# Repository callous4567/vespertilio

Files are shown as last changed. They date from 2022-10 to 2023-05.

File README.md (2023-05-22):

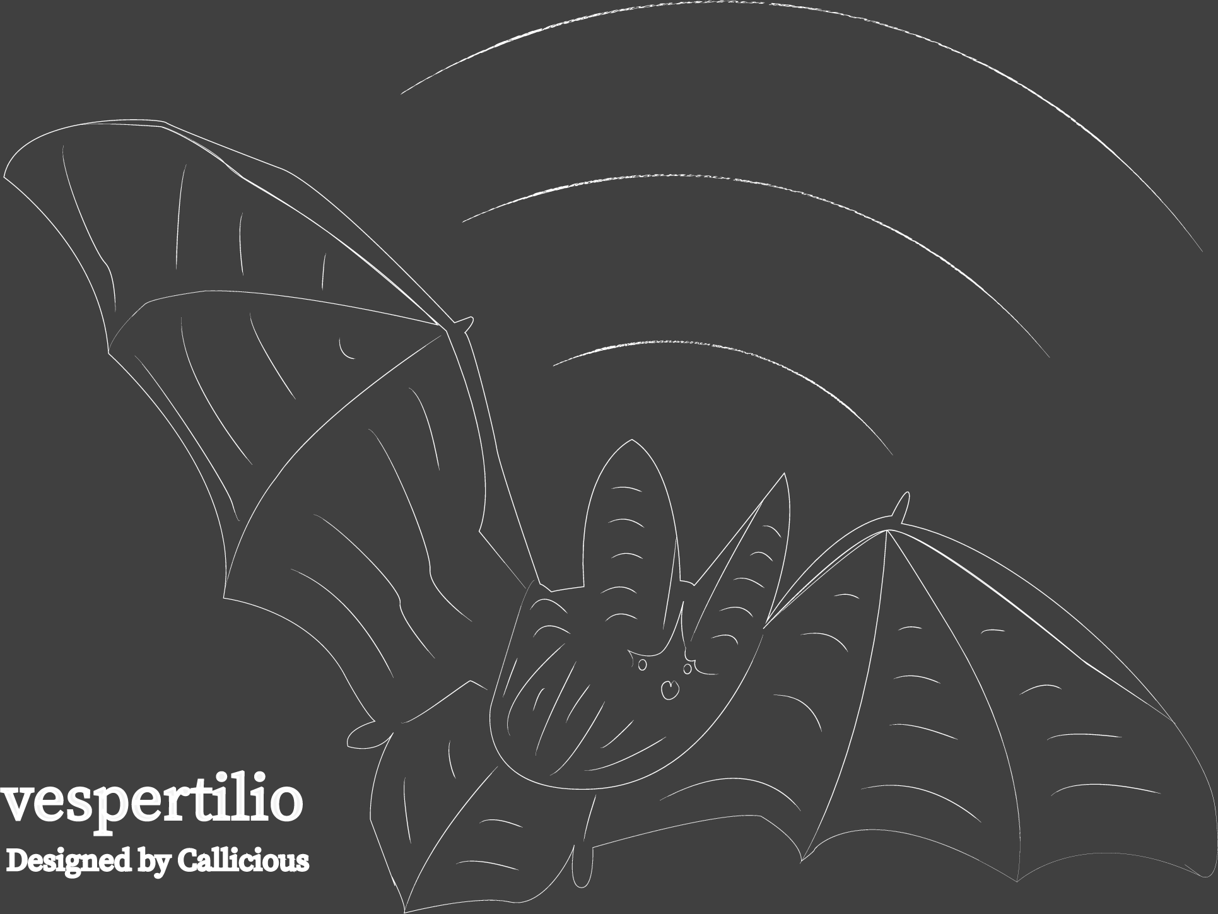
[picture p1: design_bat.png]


## General description 
A battery-powered bioacoustic recorder with a built-in ambient light sensor, and an optional weather-sensing addon attached by an onboard hijacked USB-C connector! Very much a WIP!

This is my first time with C (embedded or otherwise) and with a bunch of other things- PCBs, electronics, 3D CAD/printing/etc, so you will have to bare with me whilst I work through this project bit by bit 😅

## Where is it at the moment?
V6 design complete and functional code-wise/hardware-wise, with 75 mA power use @ 384 ksps with 12-bit internal RP2040 ADC. V9 design in progress, aiming for 50 mA power use @ 384 ksps with 16-bit dedicated ADC- hardware stage (firmware t.b.d.) 

## Features 
- BME280 for Environmental Sensing (Temp, Pressure, Humidity) as an optional attachment (attached to environmental case with 6-core custom USB-C cable!) 
- Knowles Winfrey Microphone with Differential Amplifier -> Inverting Amplifier Cascade for audio (giving single-ended-equivalent gains minimum 220+!)
- Vishay VEML6040A3OG to provide ambient light sensing of the environment
- 4-way PGA secondary gain on cascaded differential-inverting amplifier
- Compatible with usual MicroSD cards FAT32/exFAT/... @ up to 480 ksps sample rate 
- Supercapacitor on RTC allows upwards of 15 minutes to exchange batteries without losing timing configuration- no need to reconfigure after re-batterying... battery-re.. whatever!
- Competitive BOM cost: roughly £55 as of Ver 9 inclusive of weather sensor, which adds about £10 to the final cost.
- USB configurable recording schedules using desktop .exe and .json. **WIP**, allow for setting sampling frequency with each session, too, and make a GUI for configuration. **WIP**, also set the firmware over USB without having to toggle bootsel on the Pico. 

## Todo/current
- (!!!Extremely immediate!!!) Coding/Designing V9 PCB arrangement, which has 16-bit MCP33131 500ksps ADC instead, and analogue PGA switch arrangement for gain control. 
- (!!!Extremely immediate!!!) V9 PCB external regulator board design with dual MAX38640 buck regulators & 2nd-order filter design for digital power supply 
- (Delayed) Weatherproof case designs (for V6+ Audiomoth Scale, V5 done and worked fine.) 

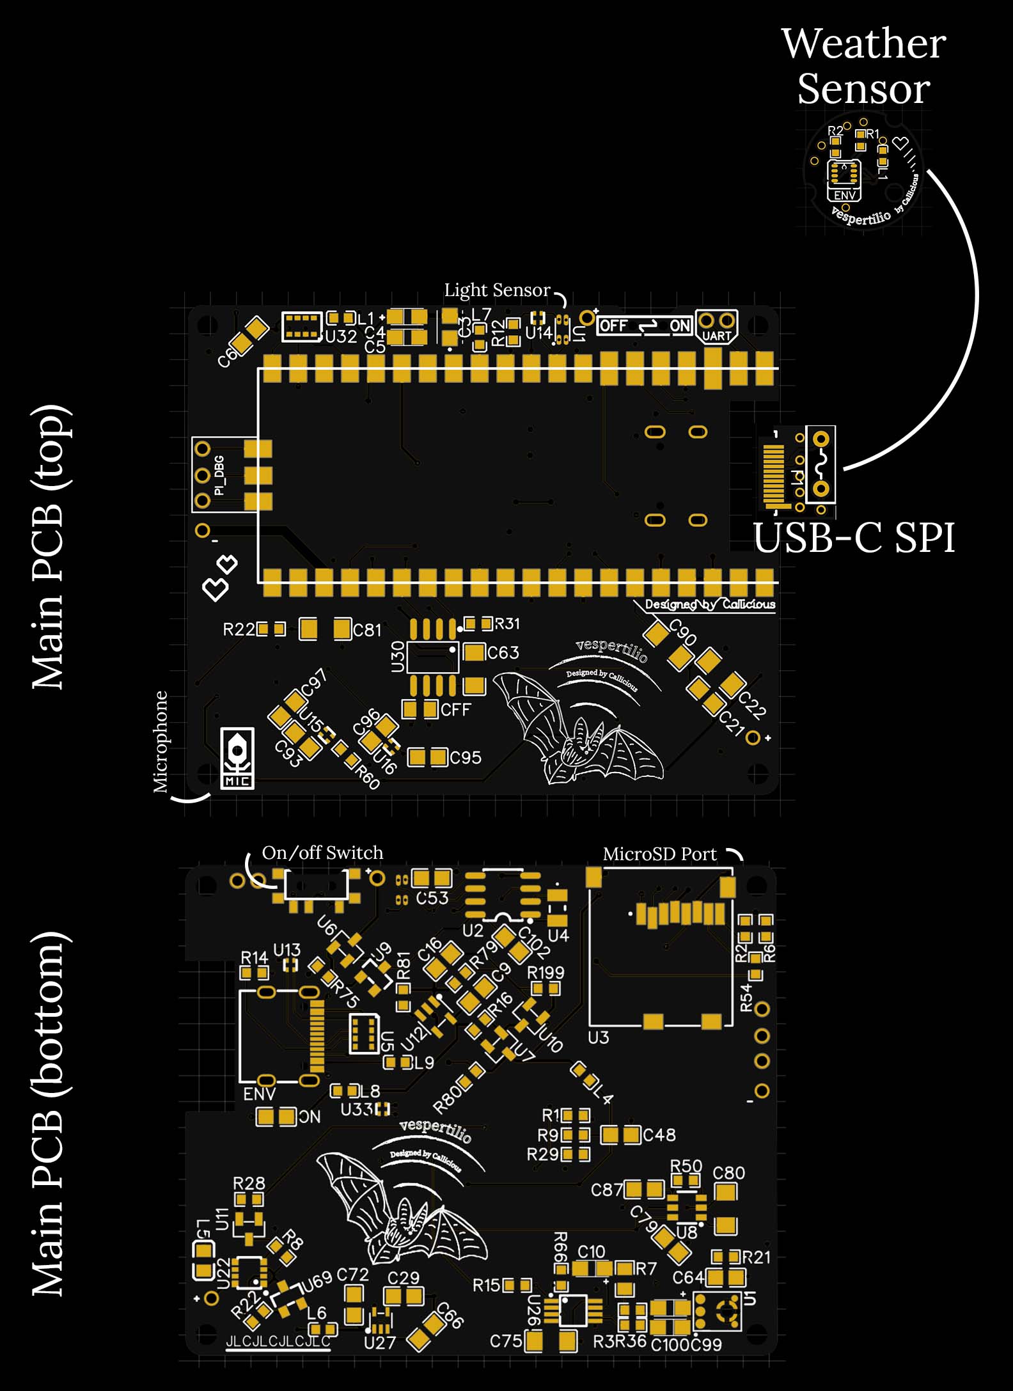
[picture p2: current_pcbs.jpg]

^*The current (outdated*) spread of PCBS and concept. vespertilio is optionally attached, by a USB-C connector manhandled into an SPI connector, to a weather module PCB.
You don't need to use the weather module- doing so costs about £10-ish. The 3D-printed case plans will allow for optional use of it. You'll note that I added that little lightmeter- U1 :)*

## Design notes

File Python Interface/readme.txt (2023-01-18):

This readme.txt will explain how to configure the vespertilio with the included JSON and executable file.
Please refer to https://github.com/callous4567/vespertilio for any updates, information on firmware updates, and so forth.

To start, set the power switch on vespertilio to OFF. 

You must first configure the vespertilio_config JSON file. 
The file will look something like this...

{
    "ADC_SAMPLE_RATE":192000,
    "RECORDING_MINUTES_PER_SUBRECORDING":5,
    "RECORDING_SESSION_LENGTH_MINUTES":120,
    "START_MINUTE":20,
    "START_HOUR":15,
    "USE_BME":true,
    "BME_PERIOD_SECONDS":3
}

ADC_SAMPLE_RATE: in Hz, sampling rate of the device. There is a limit of 499,999 (qualified on a Sandisk Ultra 64 GB to work at 480 kHz)
RECORDING_SESSION_LENGTH_MINUTES: the length of the recording session, in minutes. 
RECORDING_MINUTES_PER_SUBRECORDING: minutes per recording. We must split recording sessions to minimize number of corrupted files.
START_MINUTE: 0:59, which minute to start the recording on. By default, we start at second=0.
START_HOUR: 0:23, which hour to start the recording on.
USE_BME: true-false on whether to use environmental sensing. Note that this may add file delay. 
BME_PERIOD_SECONDS: period, in seconds, for environmental sensing. Higher = better for file delay.

Following configuration of the JSON file, you should save it and then set the power switch on vespertilio to ON.

You should then run the executable included within a minute of doing this. This executable will...

	- Parse JSON file 
	- Retrieve system time 
	- Handshake with vespertilio, send configuration to it, and tell Pico to save it to onboard flash
	- Transfer the system time to the Pico for it to configure the PCB RTC
	- Initiate a wait sequence.

Once complete, and if successful, the vespertilio will spasm its onboard LED in the colour GREEN, signifying success.

At this point, you should disconnect the USB cable and turn off the vespertilio- the order of this step doesn't matter. All success!

If you encounter any red LED flashes during this process, an error has occurred- double check your JSON with an online parser.
If the online parser says it's fine, and if you have ensured that the variables all match the same type as the template above...
Well, in that case you just have to ask me and I will check it- your device might be dogged (unlikely) or the code is busted (likely.)
Oh, or your USB cable is piss.

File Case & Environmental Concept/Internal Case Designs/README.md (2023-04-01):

# Here's the main case design that is currently running (as of PCB Ver. 4+) for the "internal case" that holds the PCB and batteries.
I've included some renders of the front and back. To mount the PCB to it, you just need some self-tapping M2 screws. To set up the battery compartment,
you'll need a soldering iron and the appropriate leaf spring battery clips from Keystone- check the BOM. Oh, and some wire that can handle at least 100 mA.
Some epoxy will help keep the battery clips in place- though it should not be necessary given I've included some indentations to avoid the clips coming loose 
(since they come with a fang to grab hold of 'em.) 

This is a WIP and all of this will be mentioned in the future guide I will write on how to build it/use it.

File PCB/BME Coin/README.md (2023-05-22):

## General description 
Ver. 1 is compatible with all model(s) before Rev. 9 of the mainboard (which is switching to I2C communication rather than SPI.) Ver.2 (t.b.d) should be used with mainboard PCB versions Rev. 9 and above.

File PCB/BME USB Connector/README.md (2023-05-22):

## General description 
Switching to I2C as of Ver. 9 of the mainboard, which will alter the pinout of the USB connector (but the same connector PCB can still be used.)

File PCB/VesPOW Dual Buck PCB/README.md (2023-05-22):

## General description 
Buck PCB to provide 3V3 and 1V1 from input VCC/batteries, with pi filters on all inputs/outputs to minimize noise. Untested and WIP for Ver. 9.

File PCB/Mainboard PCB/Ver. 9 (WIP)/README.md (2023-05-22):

## General description 
This is a placeholder to note that this is a WORK IN PROGRESS PCB! Only V6 has been qualified as fully-functional and satisfactory.

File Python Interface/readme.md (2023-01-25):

# This for the USB configuration of the device
At the moment, this is WIP. The .exe included does work- just follow readme.txt and you will be fine. 

## Planned configuration features
- Vary ADC sampling rate over sessions.
- Bootsel over USB instead of requiring use of the bootsel button on the pico. Should be easy to induce- Picoprobe does it over UART.
- GUI for the configurator- I want to make a real posh one!

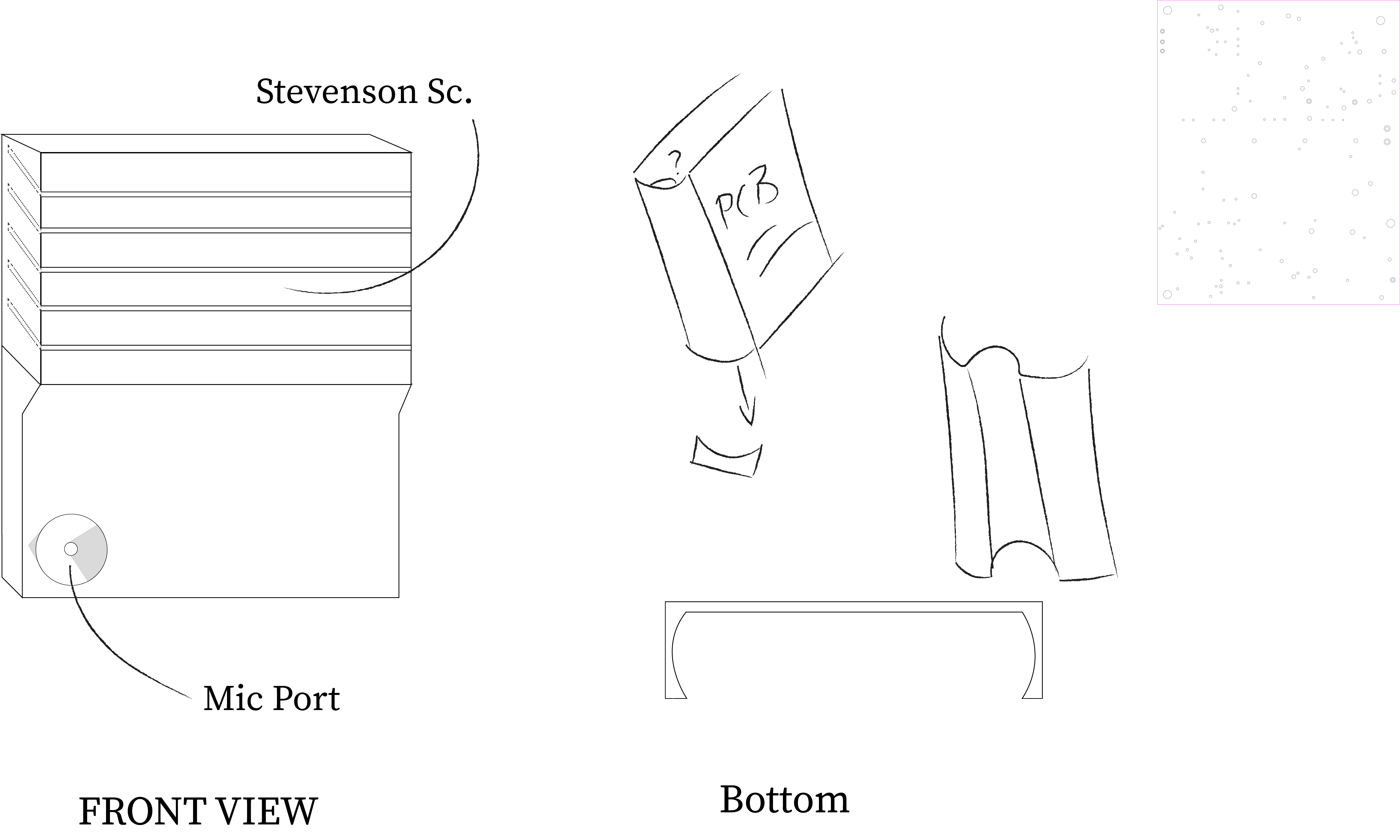
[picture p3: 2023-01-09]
PCB/Silkscreen Design Files/Ver. 3/Design for Pcb enclosure.png

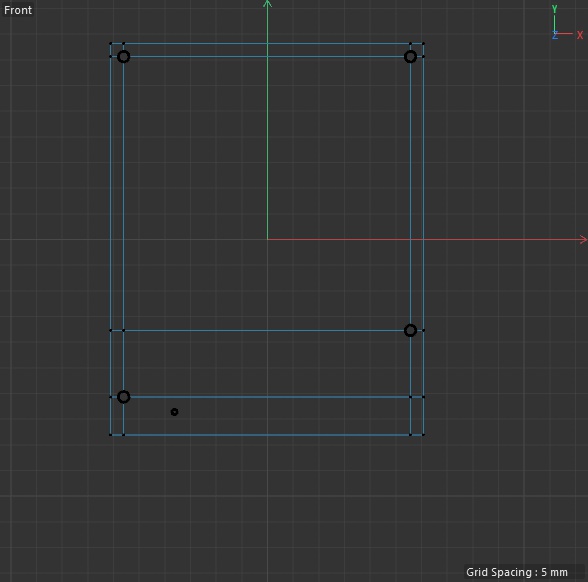
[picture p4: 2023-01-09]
PCB/Silkscreen Design Files/Ver. 3/Image.jpg

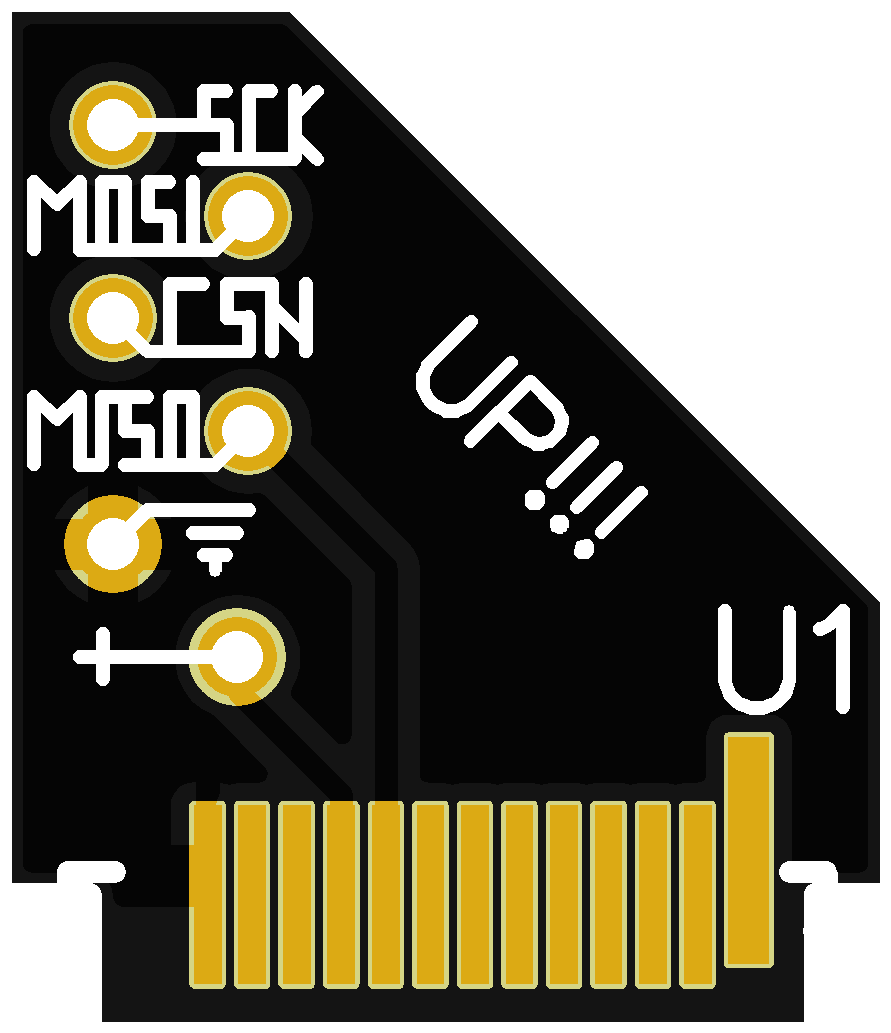
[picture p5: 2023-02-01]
PCB/BME USB Connector/Ver. 4/ex.png

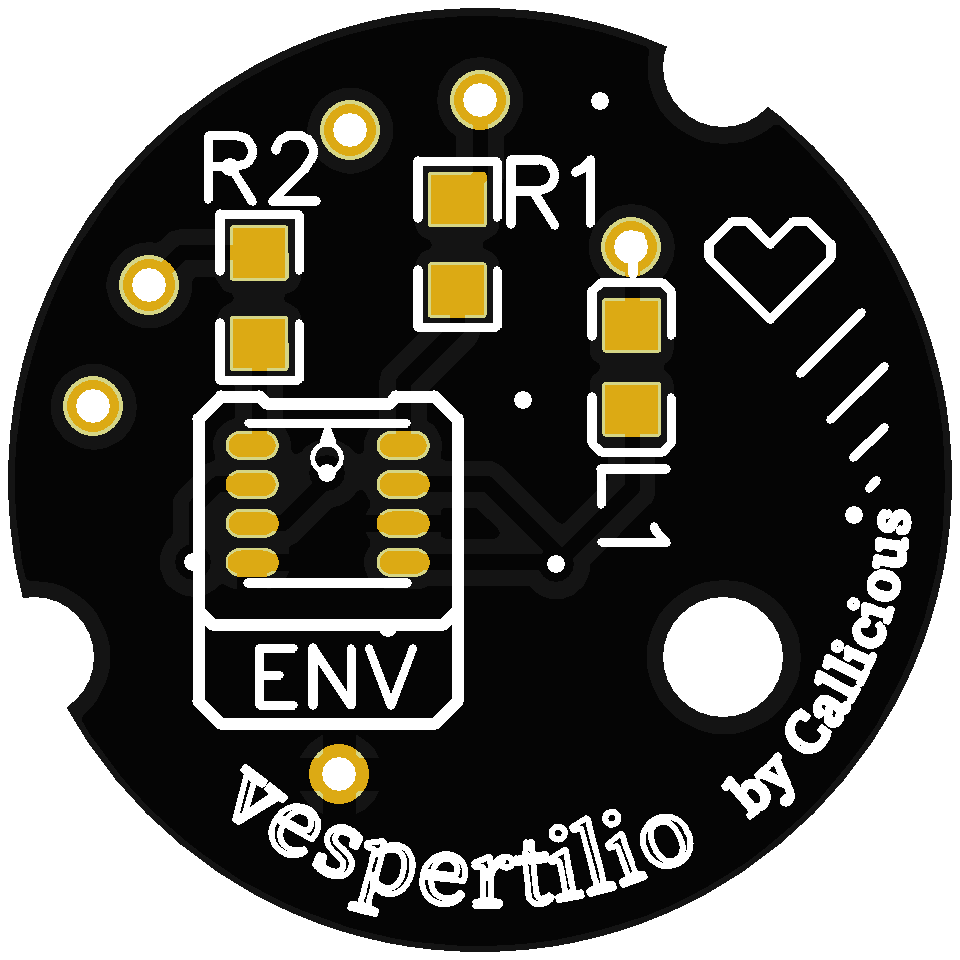
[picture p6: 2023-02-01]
PCB/BME Coin/Ver. 1/ex.png

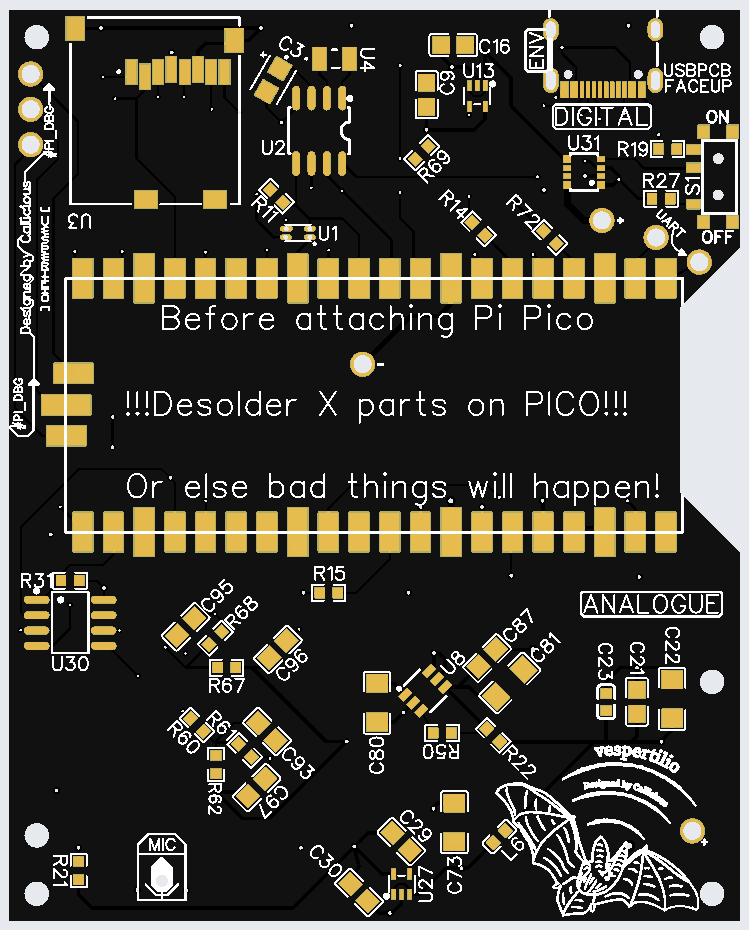
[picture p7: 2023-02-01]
PCB/Mainboard PCB/Ver. 4/ex.PNG

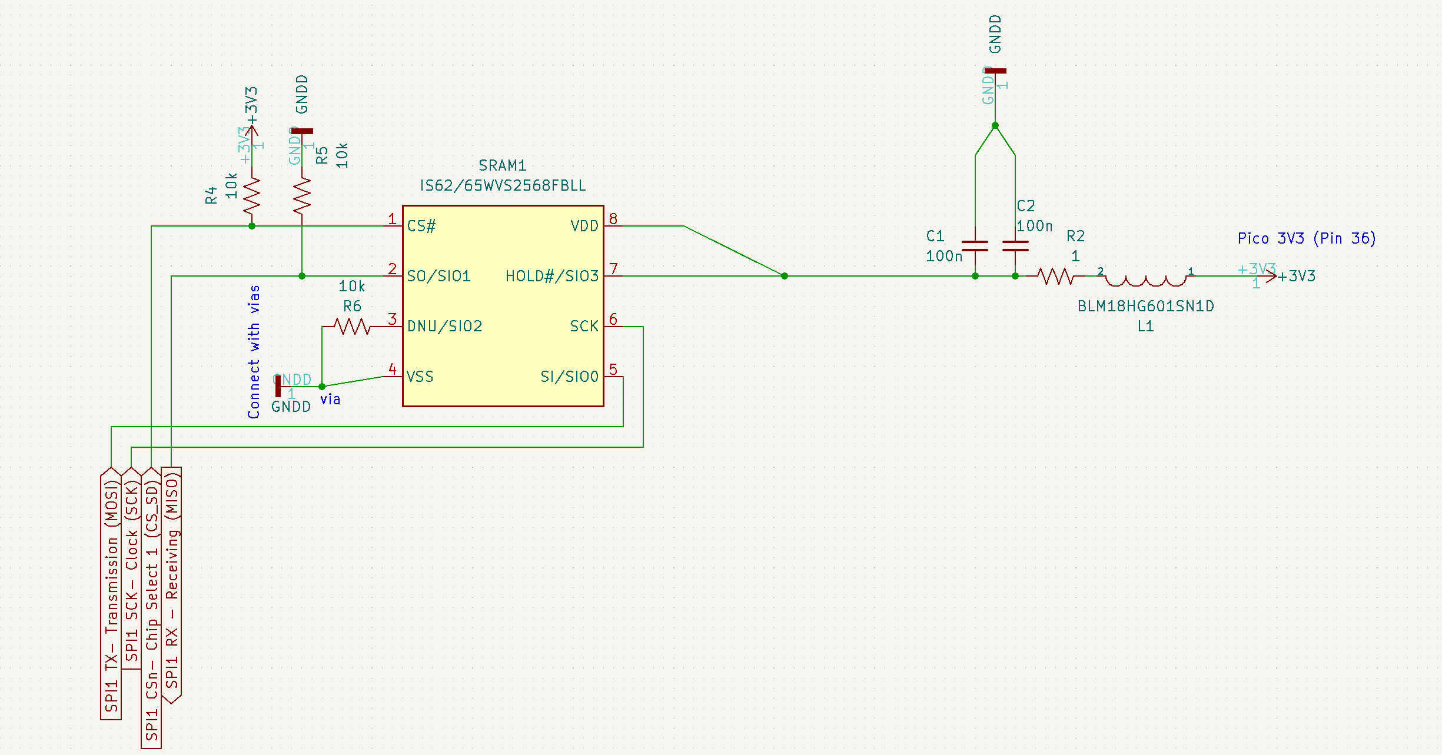
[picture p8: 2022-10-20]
IS62 SPI SRAM Driver/Circuit.PNG

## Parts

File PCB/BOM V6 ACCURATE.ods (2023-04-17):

Component | Value | Type | LCSC Part | Vendor Part | Vendor | Note | Note | Total Count | Cost Per | Total Cost
C3 | 11m | Supercap |  | CPH3225A | Digi-key | SEIKO INSTRUMENTS (VA) |  | 1 | 1.61 | 1.61
C4 | 0.1u | Tantalum | C7173 | TAJA104K035RNJ | LCSC | LOW ESR |  | 2 | 0.398 | 0.796
C5 | 10u | Tantalum | C74423 | TPSA106K010R0900 | LCSC | LOW ESR |  | 1 | 0.433 | 0.433
C6,10,99,100 | 47u | Tantalum | C131173 | TLJA476M010R0600 | LCSC |  |  | 2 | 0.207 | 0.414
C7,22,63,65,67,75,80,81,90 | 100n | MLCC | C97946 |  |  |  |  | 11 | 0.03 | 0.33
C9,16,21,64,66,72,87,93,95,102 | 10u | MLCC | C162317 |  | LCSC |  |  | 3 | 0.045 | 0.135
C29 | 10n | MLCC | C97905 |  |  |  |  | 11 | 0.063 | 0.693
C48,53,79,96,97,101 | 1u | MLCC | C527996 |  |  |  |  | 5 | 0.038 | 0.19 | Before Tax | After Tax | Total Parts
C68,83 | 1n | MLCC | C77026 |  |  |  |  | 2 | 0.034 | 0.068 | 24.8052 | 31.0065 | 119
C89 | 4.7u | MLCC | C397306 |  |  |  |  | 2 | 0.0731 | 0.1462
 |  |  |  |  |  |  |  |  |  | 0
 |  |  |  |  |  |  |  |  |  | 0
 |  |  |  |  |  |  |  |  |  | 0
 |  |  |  |  |  |  |  |  |  | 0
L1,4,6,7,8,9 | 600Ω | SMD Ferrite | C85830 | BLM18HG601SN1D | LCSC |  |  | 5 | 0.035 | 0.175
L5 | 1kΩ | SMD Ferrite |  | BLM21BD102SN1D | Mouser |  |  | 1 | 0.088 | 0.088
 |  |  |  |  |  |  |  |  |  | 0
R1,16,81 | 4.7k | Thin Film Res |  | C311913 | LCSC |  |  | 1 | 0.023 | 0.023
R2,6,12,29,31,50 | 10k | Thin Film Res |  | C311889 | LCSC |  |  | 30 | 0.023 | 0.69
R3,4,66 | 1k | Thin Film Res |  | C217840 | LCSC |  |  | 4 | 0.024 | 0.096
R8,28,79,80 | 47k | Thin Film Res |  | C311914 | LCSC |  |  | 1 | 0.023 | 0.023
R9 | 68k | Thin Film Res |  | RT0603FRE0768KL | Mouser |  |  | 1 | 0.02 | 0.02
R22(Revpol Duplicate FIX!!!),75 | 330 | Thin Film Res |  | C217969 | LCSC |  |  | 3 | 0.023 | 0.069
 | 47Ω | Thin Film Res |  | RT0603FRE0768KL | Mouser | Yageo |  | 3 | 0.02 | 0.06
R7,60,199 | 22k | Thin Film Res |  | 754-RR0816P-223D | Mouser | Susumu |  | 2 | 0.045 | 0.09
 | 0 | Thin Film Res |  | C100044 | LCSC |  |  |  |  | 0
R14,15,54 | 47Ω | Thin Film Res |  | RT0603FRE0768KL | Mouser | Yageo |  | 3 | 0.02 | 0.06
R21,22 | 100 | Thin Film Res |  | C217683 | LCSC | ARG03FTC1000 |  | 2 | 0.007 | 0.014
 |  |  |  |  |  |  |  |  |  | 0
 |  |  |  |  |  |  |  |  |  | 0
U0 |  |  |  | PICO | Pimoroni | Pi Pico OEM Chip |  | 1 | 3 | 3
U1, LIGHT |  |  | C78465 | VEML6040A3OG | LCSC | VISHAY | USE MULTILAYER PADS | 1 | 1.2 | 1.2
U2 |  |  |  | PT7C4339WEXCT-ND | Digi-key | RTC |  | 1 | 1.23 | 1.23
U3 |  |  |  | MEM2061-01-188-00-A | Farnell | MicroSD Slot |  | 1 | 0.85 | 0.85
U4 |  |  |  | 732-830054236CT-ND | Digi-key | 32.768kHz Crystal Wurth |  | 1 | 0.421 | 0.421
U5,32 |  |  |  | TC164-FR-0710KL | Mouser | 4x10k R Array |  | 2 | 0.055 | 0.11
U6,7 |  |  |  | NTR3A052PZT1G | Mouser |  |  | 2 | 0.392 | 0.784
U8 |  |  |  | MAX6070AAUT30+T | Mouser | VREF |  | 1 | 3.41 | 3.41
U9,69 |  |  |  | BZX84C15LT1G | Mouser | Zener |  | 1 | 0.128 | 0.128
U10,11 |  |  | C460977 | DMG2302UK-7 | LCSC | NFET |  | 2 | 0.0605 | 0.121
U12 |  |  |  | NCP163ASN330T1G | Mouser | LDO |  | 1 | 0.347 | 0.347
U13 |  |  |  | YC122-JR-0747RL | Mouser | 2x47 R Array |  | 1 | 0.017 | 0.017
U14,15,16,33 |  |  |  | YC122-JR-0710KL | Mouser | 2x10k R Array |  | 4 | 0.02 | 0.08
U26 |  |  |  | MAX40089AUA+ | Mouser | Op-amp Dual |  | 1 | 2.97 | 2.97 |  |  | ORDER SMT ASSEMBLY.
U27 |  |  |  | MAX8510EXK33+T | Mouser | LDO |  | 1 | 1.27 | 1.27
U30 |  |  |  | MCP4131-503E/SN | Mouser | Potentiometer |  | 1 | 0.784 | 0.784
MIC |  |  |  | SPM0687LR5H-1 | Digi-key | Winfrey |  | 1 | 1.86 | 1.86
ENV |  |  |  | TYPE-C-31-M-12 | LCSC | female Type C from LCSC C165948 |  | 1 | 7.04 | 7.04
PCB |  |  |  | Custom | JLCPCB | Custom |  | 1 | 2 | 2
Case |  |  |  | Custom | JLCPCB/3D | Custom |  | 1 | 5 | 5
S1 |  |  |  | 710-450404015514 | Mouser | Wurth Switch |  | 1 | 0.7 | 0.7
 |  |  |  |  |  |  |  |  |  | 0
 |  |  |  |  |  |  |  |  |  | 0
 |  |  |  |  |  |  |  |  |  | 0
FOR THE BME PCB! |  |  |  |  |  |  |  | 1 | 1.24 | 1.24
C5 | 4.7u | MLCC | C397306 |  | LCSC |  |  | 1 | 0.0731 | 0.0731
C67 | 100n | MLCC | C97946 |  | LCSC |  |  | 1 | 0.03 | 0.03
L1 | 600Ω | SMD Ferrite | C85830 | BLM18HG601SN1D | LCSC |  |  | 1 | 0.035 | 0.035
R1,2,3 | 47Ω | Thin Film Res |  | RT0603FRE0768KL | Mouser | Yageo |  | 3 | 0.02 | 0.06
U6 |  |  |  | BME280/680/688 | Mouser |  |  | 1 | 7 | 7
 |  |  |  |  |  |  |  |  |  | Sum
 |  |  |  |  |  |  |  |  |  | 47.9833

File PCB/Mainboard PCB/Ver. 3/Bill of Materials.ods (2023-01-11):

Component | Value | Type | LCSC Part | Vendor Part | Vendor | Note | Note | Total Count | Cost Per | Total Cost
C1 | 10u | Tantalum |  | TPSB106K016R0500 | Mouser |  |  | 1 | 0.433 | 0.433
C2,58 | 0.1u | Tantalum |  | TAJR104K035RNJ | Mouser |  |  | 2 | 0.398 | 0.796
U28,29 | 1u | Tantalum |  | TAJR105K010RNJ | LCSC |  |  | 2 | 0.207 | 0.414
C3 | 11m | Supercap |  | CPH3225A | Digi-key | SEIKO INSTRUMENTS (VA) |  | 1 | 1.61 | 1.61
C5,54,89 | 4.7u | MLCC | C397306 |  | LCSC |  |  | 3 | 0.045 | 0.135
C6,16,21,48,60,64,66,72,87,93,95 | 10u | MLCC | C162317 |  | LCSC |  |  | 11 | 0.03 | 0.33
C7,22,63,65,67,73,75,80,81,90,92 | 100n | MLCC | C97946 |  | LCSC |  |  | 11 | 0.063 | 0.693
C8,29,61,70,82 | 10n | MLCC | C97905 |  | LCSC |  |  | 5 | 0.038 | 0.19 | Before Tax | After Tax | Total Parts
C9,14,30,53,79,96,97 | 1u | MLCC | C527996 |  | LCSC |  |  | 7 | 0.033 | 0.231 | 39.836 | 49.795 | 118
C23,69 | 100p | MLCC | C71664 |  | LCSC |  |  | 2 | 0.034 | 0.068
C24 | 10n | Film |  | ECH-U1C103JX5 | Mouser |  | Get | 1 | 0.417 | 0.417
C68,83 | 1n | MLCC | C77026 |  | LCSC |  |  | 2 | 0.034 | 0.068
L1,2,3,4,6 | 600Ω | SMD Ferrite | C85830 | BLM18HG601SN1D | LCSC |  |  | 5 | 0.035 | 0.175
L5 | 1kΩ | SMD Ferrite |  | BLM21BD102SN1D | Mouser |  |  | 1 | 0.088 | 0.088
 |  |  |  |  |  |  |  |  |  | 0
R1 | 4.7k | Thin Film Res |  | C311913 | LCSC |  |  | 1 | 0.023 | 0.023
R2,4,5,6,7,10,11,12,13,14,15,16,17,27,28,29,31,34,35,50,51,52,53,59,60,61,62,63,67,68 | 10k | Thin Film Res |  | C311889 | LCSC |  |  | 30 | 0.023 | 0.69
R3,19,36,66 | 1k | Thin Film Res |  | C217840 | LCSC |  |  | 4 | 0.024 | 0.096
R8 | 47k | Thin Film Res |  | C311914 | LCSC |  |  | 1 | 0.023 | 0.023
R9 | 68k | Thin Film Res |  | RT0603FRE0768KL | Mouser |  |  | 1 | 0.02 | 0.02
R18,21,22 | 330 | Thin Film Res |  | C217969 | LCSC |  |  | 3 | 0.023 | 0.069
R20,54,55 | 47 | Thin Film Res |  | RT0603FRE0747RL | Mouser |  | Get | 3 | 0.02 | 0.06
U0 |  |  |  | PICO | Pimoroni | Pi Pico OEM Chip |  | 1 | 3 | 3
U1 |  |  |  | 710-450404015514 | Mouser | Wurth Switch |  | 1 | 0.7 | 0.7
U2 |  |  |  | PT7C4339WEXCT-ND | Digi-key | RTC |  | 1 | 1.23 | 1.23
U3 |  |  |  | MEM2061-01-188-00-A | Farnell | MicroSD Slot |  | 1 | 0.85 | 0.85
U4 |  |  |  | 732-830054236CT-ND | Digi-key | 32.768kHz Crystal Wurth |  | 1 | 0.421 | 0.421
U5 |  |  |  | FDS9926A | Farnell | Dual NFET FDS9926A |  | 1 | 0.558 | 0.558
U6 |  |  |  | BME280 | Mouser | BME280 Sensor |  | 1 | 7.04 | 7.04
U7 |  |  |  | NTR3A052PZT1G | Mouser | PFET | Get | 1 | 0.392 | 0.392
U8 |  |  |  | MAX6070AAUT30+T | Mouser | VREF |  | 1 | 3.41 | 3.41
U11,22 |  |  |  | ECH8654-TL-H | Mouser | PFET Dual |  | 2 | 0.638 | 1.276
U12,21 |  |  |  | BZX84C15LT1G | Mouser | Zener |  | 2 | 0.128 | 0.256
U13,27 |  |  |  | MAX8510EXK33+T | Mouser | Regulator |  | 2 | 1.27 | 2.54
U26 |  |  |  | MAX40089AUA+ | Mouser | Op-amp Dual |  | 1 | 2.97 | 2.97
U30 |  |  |  | MCP4131-503E/SN | Mouser | Potentiometer |  | 1 | 0.784 | 0.784
MIC |  |  |  | SPM0687LR5H-1 | Digi-key | Winfrey |  | 1 | 1.86 | 1.86
PCB |  |  |  | Custom | JLCPCB | Custom |  | 1 | 1.68 | 1.68
Battery Holder |  |  |  | MP000331 | Farnell |  |  | 1 | 1.24 | 1.24
Case |  |  |  | Custom | JLCPCB/3D | Custom |  | 1 | 3 | 3

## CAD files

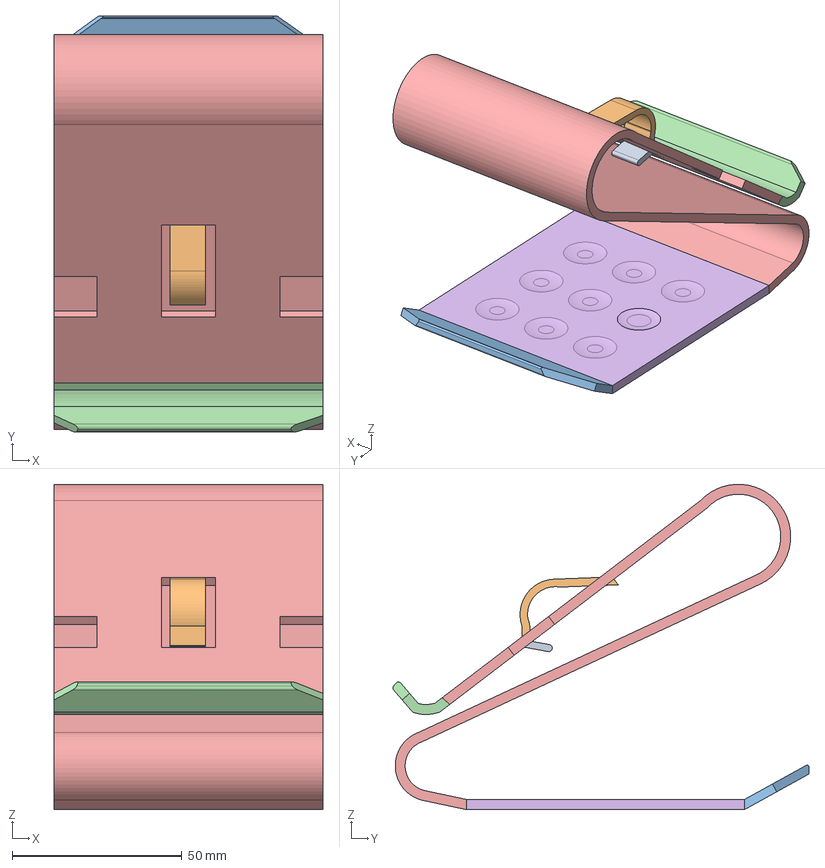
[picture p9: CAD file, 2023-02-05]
Case & Environmental Concept/Battery Contact Models/209.stp
79.2 x 122.6 x 95.9 mm

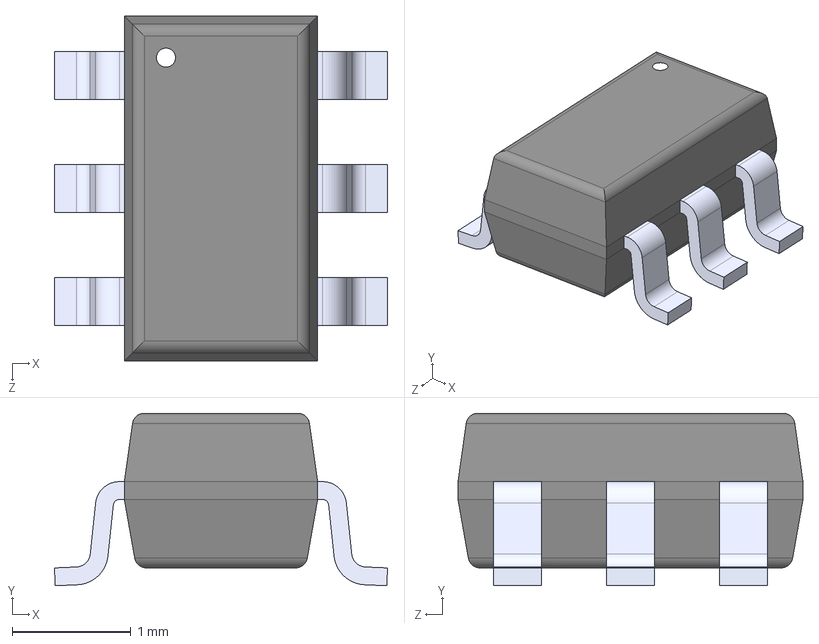
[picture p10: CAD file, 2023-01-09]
Various Datasheets & Schematics/MaximReference/MAX6071AAUT30T.step
2.80 x 1.45 x 2.90 mm

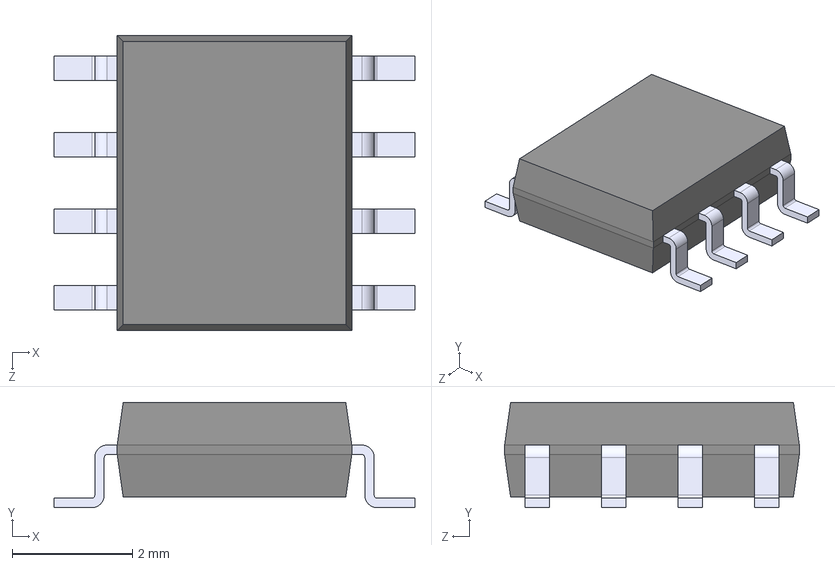
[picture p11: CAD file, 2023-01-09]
Various Datasheets & Schematics/MCP4131 Potentiometer/MCP4131-103E_SN.step
6.00 x 1.75 x 4.90 mm

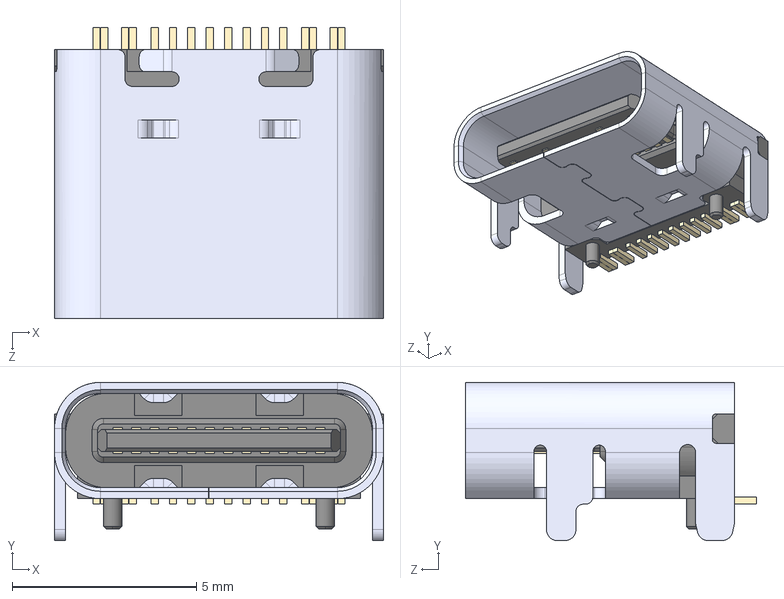
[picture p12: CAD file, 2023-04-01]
Various Datasheets & Schematics/USB-C Female TYPE-C-31-M-12/TYPE-C-31-M-12.step
8.94 x 4.30 x 7.90 mm

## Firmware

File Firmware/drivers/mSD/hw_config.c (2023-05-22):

/* hw_config.c
Copyright 2021 Carl John Kugler III
Licensed under the Apache License, Version 2.0 (the License); you may not use 
this file except in compliance with the License. You may obtain a copy of the 
License at
   http://www.apache.org/licenses/LICENSE-2.0 
Unless required by applicable law or agreed to in writing, software distributed 
under the License is distributed on an AS IS BASIS, WITHOUT WARRANTIES OR 
CONDITIONS OF ANY KIND, either express or implied. See the License for the 
specific language governing permissions and limitations under the License.
*/
/*
This file should be tailored to match the hardware design.
There should be one element of the spi[] array for each hardware SPI used.
There should be one element of the sd_cards[] array for each SD card slot.
The name is should correspond to the FatFs "logical drive" identifier.
(See http://elm-chan.org/fsw/ff/doc/filename.html#vol)
The rest of the constants will depend on the type of
socket, which SPI it is driven by, and how it is wired.
*/

#include <string.h>
//
#include "my_debug.h"
//
#include "hw_config.h"
//
#include "ff.h" /* Obtains integer types */
//
#include "diskio.h" /* Declarations of disk functions */

void spi1_dma_isr();

// All the SRAM parameters for the SD CARD for the hardware configuration. You will need to manually copy these over to hw_config.c sadly. 
static const int SD_SPI_RX_PIN = 12;// Yellow 
static const int SD_SPI_CSN_PIN = 13; // White 
static const int SD_SPI_SCK_PIN = 14; // Blue
static const int SD_SPI_TX_PIN =  15; // Green 
static const int SD_BAUDRATE = 26*1000*1000; // 45*1000*1000; 

// The hardware configuration for the SD card we're using. 
static spi_t spis[] = {  // One for each SPI.
    {

        .hw_inst = spi1,  
        .miso_gpio = SD_SPI_RX_PIN, 
        .mosi_gpio = SD_SPI_TX_PIN, 
        .sck_gpio = SD_SPI_SCK_PIN,
        .baud_rate = SD_BAUDRATE,  // The limitation here is SPI slew rate.
        .dma_isr = spi1_dma_isr,
        .mosi_gpio_drive_strength = GPIO_DRIVE_STRENGTH_2MA,
        .sck_gpio_drive_strength = GPIO_DRIVE_STRENGTH_2MA,
        .set_drive_strength = true,
    }
};

// Hardware Configuration of the SD Card "objects"
static sd_card_t sd_cards[] = {  // One for each SD card
    {
        .pcName = "0",           // Name used to mount device
        .spi = &spis[0],          // Pointer to the SPI driving this card
        .ss_gpio = SD_SPI_CSN_PIN,            // The SPI slave select GPIO for this SD card
        .use_card_detect = false,
        .card_detect_gpio = 21,   // Card detect
        .card_detected_true = -1,  // What the GPIO read returns when a card is
                                  // present. Use -1 if there is no card detect.
        .m_Status = STA_NOINIT
    }
};

void spi1_dma_isr() { spi_irq_handler(&spis[0]); }

/* ********************************************************************** */
size_t sd_get_num() { return count_of(sd_cards); }
sd_card_t *sd_get_by_num(size_t num) {
    if (num <= sd_get_num()) {
        return &sd_cards[num];
    } else {
        return NULL;
    }
}
size_t spi_get_num() { return count_of(spis); }
spi_t *spi_get_by_num(size_t num) {
    if (num <= sd_get_num()) {
        return &spis[num];
    } else {
        return NULL;
    }
}

/* [] END OF FILE */

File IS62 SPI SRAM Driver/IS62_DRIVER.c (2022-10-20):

#include <stdio.h>
#include <string.h>
#include "pico/stdlib.h"
#include "pico/binary_info.h"
#include "hardware/spi.h"
#include "hardware/vreg.h"
#include "hardware/clocks.h"
#include "hardware/adc.h"
#include "hardware/rtc.h"
#include "pico/util/datetime.h"
#include "hardware/dma.h"

// All the SRAM parameters 
static const int SPI_RX_PIN = 12;// Yellow 
static const int SPI_CSN_PIN = 13; // White 
static const int SPI_SCK_PIN = 14; // Blue
static const int SPI_TX_PIN =  15; // Green 
static const int BAUDRATE = 22000000; // Hz 
spi_inst_t *SPI = spi1; // which SPI 
static const uint8_t READ = 0b00000011; 
static const uint8_t WRITE = 0b00000010;
static const uint8_t RDMR = 0b00000101; 
static const uint8_t WRMR = 0b00000001;
static const int MAX_BYTE = 262144; 
static const int MAX_PAGE = 8192;
static const int PAGE_SIZE_BYTES = 32;
static const int PAGE_SIZE_BITS = 256;

// The ADC parameters. Note that we output ADC samples as 16-bit values (12bit -> 16bit.)
static const int ADC_PIN = 26;
static const int ADC_SAMPLE_RATE = 192000;
static const int ADC_TRANSFER_SIZE = 512; // 256 transfers equals 512 bytes equals 16 pages. 

// Print as binary the individual byte a 
static void toBinary(uint8_t a) {
    uint8_t i;

    for(i=0x80;i!=0;i>>=1)
        printf("%c",(a&i)?'1':'0'); 
    printf("\r\n");
}
static void toBinary_16(uint16_t a) {
    uint16_t i;

    for (int i = 0; i < 16; i++) {
        printf("%d", (a & 0x8000) >> 15);
        a <<= 1;
    }
    printf("\r\n");
}

// Activate the CS pin (pull low)
static inline void cs_select() { /* declaration: https://stackoverflow.com/questions/21835664/why-declare-a-c-function-as-static-inline 
    declaring static means other modules do not see it: it's local to this module and saves effort
    on letting other modules see it.
    declaring inline means that when the file is compiled, cs_select() will be dumped inline in the code,
    and then compiled locally, rather than being pulled in some it having been compiled elsewhere.
    declaring void means that this function does not return anything at all. 
    */
    //asm volatile("nop \n nop \n nop"); // assembler-up some nops- delay code by 3 clock cycles.
    gpio_put(SPI_CSN_PIN, 0); // pull low/active
    //asm volatile("nop \n nop \n nop"); // https://forums.raspberrypi.com/viewtopic.php?t=332078
}
static inline void cs_deselect() {
    
    //asm volatile("nop \n nop \n nop"); // assembler-up some nops- delay code by 3 clock cycles.
    gpio_put(SPI_CSN_PIN, 1); // pull high/active
    //asm volatile("nop \n nop \n nop"); // https://forums.raspberrypi.com/viewtopic.php?t=332078
}

// Test writing/reading the register- use before read_default_register(). Default PAGE MODE.
static void write_default_register() {
    uint8_t buf[2]; // first the instruction then the new register 
    buf[0] = WRMR;
    buf[1] = 0b10000000;
    cs_select();
    int written = spi_write_blocking(SPI, buf, 2);
    cs_deselect();
    printf("Bytes written to SPI... ");
    printf("%d", written);
    printf("\r\n");
}
static void read_default_register() {
    uint8_t buf[1];
    buf[0] = RDMR;
    cs_select();
    spi_write_blocking(SPI, buf, 1);
    spi_read_blocking(SPI, 0, buf, 1);
    cs_deselect();
    printf("The current read register...\r\n");
    toBinary(buf[0]);
}

// Set mode
static inline void byte_mode() {
    uint8_t buf[2]; // first the instruction then the new register 
    buf[0] = WRMR;
    buf[1] = 0b00000000;
    cs_select();
    spi_write_blocking(SPI, buf, 2);
    cs_deselect();
}
static inline void page_mode() {
    uint8_t buf[2]; // first the instruction then the new register 
    buf[0] = WRMR;
    buf[1] = 0b10000000;
    cs_select();
    spi_write_blocking(SPI, buf, 2);
    cs_deselect();
}
static inline void sequential_mode() {
    uint8_t buf[2]; // first the instruction then the new register 
    buf[0] = WRMR;
    buf[1] = 0b01000000;
    cs_select();
    spi_write_blocking(SPI, buf, 2);
    cs_deselect();
}

// Set the SPI mode to 8 bit or 16 bit as required below
static inline void SPI8() {
    spi_set_format(SPI, 8, SPI_CPOL_0, SPI_CPHA_0, SPI_MSB_FIRST);
}
static inline void SPI16() {
    spi_set_format(SPI, 16, SPI_CPOL_0, SPI_CPHA_0, SPI_MSB_FIRST);
}

// Start sequentials. Note that you need to call SPI8() at the end of any 16-bit process for future commands (8 bit) to work. When in 16-bit, you have half of MAX_BYTE/PAGE for indices. 
static inline void start_sequential_read(int address) {
    uint8_t buf[4];
    buf[0] = READ;
    buf[1] = 0b000000 | (address >> 16);
    buf[2] = address >> 8;
    buf[3] = address; 
    cs_select();
    spi_write_blocking(SPI, buf, 4);
}
static inline void start_sequential_read16(int address) {
    uint8_t buf[4];
    buf[0] = READ;
    buf[1] = 0b000000 | (address >> 16);
    buf[2] = address >> 8;
    buf[3] = address; 
    cs_select();
    spi_write_blocking(SPI, buf, 4);
    SPI16();
}
static inline void start_sequential_write(int address) {
    uint8_t buf[4];
    buf[0] = WRITE;
    buf[1] = 0b000000 | (address >> 16);
    buf[2] = address >> 8;
    buf[3] = address; 
    cs_select();
    spi_write_blocking(SPI, buf, 4);
}
static inline void start_sequential_write16(int address) {
    uint8_t buf[4];
    buf[0] = WRITE;
    buf[1] = 0b000000 | (address >> 16);
    buf[2] = address >> 8;
    buf[3] = address; 
    cs_select();
    spi_write_blocking(SPI, buf, 4);
    SPI16();
}

// Read a certain byte
static inline uint8_t read_byte(int address) {
    uint8_t buf[4];
    uint8_t read_buf[1];
    buf[0] = READ;
    buf[1] = 0b000000 | (address >> 16);
    buf[2] = address >> 8;
    buf[3] = address;
    cs_select();
    spi_write_blocking(SPI, buf, 4);
    spi_read_blocking(SPI, 0x00, read_buf, 1);
    cs_deselect();
    return read_buf[0];
}
static inline uint8_t write_byte(int address, uint8_t byte) {
    uint8_t buf[5];
    buf[0] = WRITE;
    buf[1] = 0b000000 | (address >> 16);
    buf[2] = address >> 8;
    buf[3] = address;
    buf[4] = byte;
    cs_select();
    spi_write_blocking(SPI, buf, 5);
    cs_deselect();
}

// Set the entire SRAM unit to ZERO 
static void SRAM_zeros() {
    sequential_mode();
    int i = 0;
    uint8_t zero_page[512]; // 16 pages 
    while (i<512) {
        zero_page[i] = 0b00000000;
        i += 1;
    }
    i = 0;
    int n_page_writes = (MAX_PAGE/16) - 1; 
    start_sequential_write(0);
    while (i <= n_page_writes) {
        spi_write_blocking(SPI, zero_page, 512);
        i += 1; 
    }
    cs_deselect();
}
static void SRAM_ones() {
    /*
    // Do a sequential test... (it works fine!) 
    printf("Now sequential mode tests! \r\n");
    SRAM_zeros();
    byte_mode();
    uint8_t TT1 = read_byte(MAX_BYTE-1);
    toBinary(TT1);
    SRAM_ones();
    byte_mode();
    uint8_t TT2 = read_byte(MAX_BYTE-1);
    toBinary(TT2);
    */
    int i = 0;
    uint8_t one_page[512]; // 16 pages
    while (i<512) {
        one_page[i] = 0b11111111;
        i += 1;
    }
    i = 0;
    int n_page_writes = (MAX_PAGE/16) - 1; 
    sequential_mode();
    start_sequential_write(0);
    while (i <= n_page_writes) {
        spi_write_blocking(SPI, one_page, 512);
        i += 1; 
    }
    cs_deselect();
}
static void SRAM_decimals() { 
    int i = 0;
    uint8_t buf[1];
    sequential_mode();
    start_sequential_write(0);
    while (i<513) {
        write_byte(i, i);
        i += 1;
    }
    cs_deselect();
    /*
    SRAM_decimals();
    byte_mode();
    int i = 0;
    while (i < 512) {
        toBinary(read_byte(i));
        i += 1;
    }
    */
}
/*
static void READ_all() {


    // Initiate the RTC
    datetime_t t = {
        .year = 2022,
        .month = 10,
        .day = 20,
        .dotw = 4,
        .hour = 17,
        .min = 50,
        .sec = 00
    };
    rtc_init();
    rtc_set_datetime(&t);
    sleep_us(64);

    // Print time 
    char datetime_buf[256];
    char *datetime_str = &datetime_buf[0];
    rtc_get_datetime(&t);
    datetime_to_str(datetime_str, sizeof(datetime_buf), &t);
    printf("Start time for writing test ... \r%s      \r\n", datetime_str);
    int i = 0;
    while (i < 100) {
        SRAM_ones();
        i += 1;
    }
    rtc_get_datetime(&t);
    datetime_to_str(datetime_str, sizeof(datetime_buf), &t);
    printf("End time for writing test... \r%s      \r\n", datetime_str);

    // Print time 
    rtc_get_datetime(&t);
    datetime_to_str(datetime_str, sizeof(datetime_buf), &t);
    printf("Start time for reading test ... \r%s      \r\n", datetime_str);
    i = 0;
    while (i < 100) {
        READ_all();
        i += 1;
    }
    rtc_get_datetime(&t);
    datetime_to_str(datetime_str, sizeof(datetime_buf), &t);
    printf("End time for reading test... \r%s      \r\n", datetime_str);


    sequential_mode();
    uint8_t temp_buffer[512];
    int n_reads = MAX_BYTE/512 - 1;
    int i = 0;
    start_sequential_read(0);
    while (i <= n_reads) {
        spi_read_blocking(SPI, 0x00, temp_buffer, 512);
        i += 1;
    }
    cs_deselect();
}
*/

// Set up the clock divisor: check documentation to convince yourself we did this right. 
static inline void adc_clock_divisor() {
    int divider = (48000000 - ADC_SAMPLE_RATE)/ADC_SAMPLE_RATE;
    adc_set_clkdiv(divider);
}

// Initialize the ADC taking from default pin
static inline void setup_adc() {
    adc_init();
    adc_gpio_init(ADC_PIN);
    adc_select_input(ADC_PIN - 26); // select input from appropriate input
    adc_clock_divisor();
    adc_fifo_setup(true, true, 4, false, false);
}

// Initialize the main 
int main() {

    // Sleep a bit for SRAM to stabilise
    sleep_ms(1000);
    stdio_init_all();

    // Initialize our SPI bus 
    spi_init(SPI, BAUDRATE);
    SPI8();

    // Setup pins 
    gpio_init(SPI_CSN_PIN);
    gpio_set_dir(SPI_CSN_PIN, true);

    // Set pin funcionality to the SPI bus 
    gpio_set_function(SPI_RX_PIN, GPIO_FUNC_SPI); // https://raspberrypi.github.io/pico-sdk-doxygen/group__hardware__gpio.html
    gpio_set_function(SPI_SCK_PIN, GPIO_FUNC_SPI); // j is enumerated- see the documentation 
    gpio_set_function(SPI_TX_PIN, GPIO_FUNC_SPI);
    
    // Reset the SRAM
    SRAM_zeros();

    // Set up ADC Fifo (free-running mode!) (one transfer is one sample is two bytes.) 
    setup_adc();

    // Configure DMA channel from ADC to the SPI output FIFO
    int ADC_DMA_CHAN = dma_claim_unused_channel(true);
    dma_channel_config ADC_DMA_CONF = dma_channel_get_default_config(ADC_DMA_CHAN);
    channel_config_set_transfer_data_size(&ADC_DMA_CONF, DMA_SIZE_16);
    channel_config_set_read_increment(&ADC_DMA_CONF, false);
    channel_config_set_write_increment(&ADC_DMA_CONF, false);
    channel_config_set_dreq(&ADC_DMA_CONF, DREQ_ADC);
    dma_channel_configure(
        ADC_DMA_CHAN,
        &ADC_DMA_CONF,
        &spi1_hw->dr,
        &adc_hw->fifo,
        ADC_TRANSFER_SIZE, 
        false
    );
    adc_fifo_drain();

    // Start sequential write mode
    sequential_mode();
    start_sequential_write16(0);
    dma_start_channel_mask(1u << ADC_DMA_CHAN);
    adc_run(true);
    dma_channel_wait_for_finish_blocking(ADC_DMA_CHAN);
    cs_deselect();
    SPI8();
    adc_run(false);
    adc_fifo_drain(); 

    // Test reading the first few bytes!
    printf("\r\n");
    uint16_t buf[ADC_TRANSFER_SIZE];
    start_sequential_read16(0);
    spi_read16_blocking(SPI, 0x00, buf, ADC_TRANSFER_SIZE);
    cs_deselect();
    SPI8();
    for (int k = 0; k < ADC_TRANSFER_SIZE; k++) {
        printf("%u \r\n", buf[k]);
    }

    /*
    This is reliable
    Setting the max number of transfers is reliable
    Writes as 16 bit values (not 12 bit) 
    So far, so good! :D 
    */
}

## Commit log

2022-10-20 Circuit diagrams and extra errata
    because why not.
2023-01-09 A whole lot of stuff
    Lots!
    [MAX6071AAUT30T.step, MCP4131-103E_SN.step]
2023-01-11 Update Gerber_PCB_Batcorder_4LAYER.zip
    Update PCB
2023-01-11 Create Bill of Materials.ods
    [Bill of Materials.ods]
2023-01-16 Single-thread recording
    Reliant on a race condition but here it is. Once I understand the SD write protocol more, I will modify this to not be race-condition-dependent, instead just dumping straight to the SD as it runs in 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
2023-01-18 Lots
    Fix configuration .exe
    Single-threaded recording finally works (t.b.d BME280 on this)
    Tested to record 499.999 kHz audio perfectly to MicroSD
    Files now correctly get timestamps using Pico RTC and external RTC (ext RTC used to update internal RTC)
    Modified FatFS to allow f_write to write entire files at once straight from DMA bytebuffers of finite 512-byte size
2023-01-22 Case concept
    also the readme.
    [Bill of Materials.ods]
2023-01-25 Prepare for Ver. 4
    Ver.4 of PCB is being prepared in anticipation of externalizing BME280/BME688, adding ambient light sensor, and various other changes.
    [Bill of Materials.ods]
2023-01-25 .
    Clean things up a bit
    [MAX6071AAUT30T.step, MCP4131-103E_SN.step]
2023-01-31 various
    .
    [Bill of Materials.ods]
2023-02-01 Various
    Update PCBs to V4 complete + order.
2023-02-05 Various models
    Model/adapt Keystone battery contact models + change internal case design to reduce weight
2023-02-05 Finished internal battery case
    need to put inside main internal case
    [209.stp]
2023-02-06 Update main.c4d
    Now we have finished the internal case designs- pazzazzed 'em up a bit.
2023-02-08 Update main.c4d
    Make it more printable.
2023-02-16 Circuit Schemas
    WIP need to update from PCB.
    [Analogue Circuitry.kicad_pcb, Analogue Circuitry.kicad_sch, BME280.kicad_pcb, BME280.kicad_sch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]
2023-04-01 Whole boatload of changes
    Latest.
    [Analogue Circuitry.kicad_sch, BME280.kicad_sch, MicroSD.kicad_sch, Pico MCU.kicad_sch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]
2023-04-05 1
    1
    [Analogue Circuitry.kicad_sch, full.kicad_pcb, full.kicad_sch]
2023-04-17 Bunch of changes
    and I'm a lazy mofo who doesn't want to version control my directory and so yeah
    [Analogue Circuitry.kicad_sch, BOM V6 ACCURATE.ods]
2023-04-26 Bunch of changes
    Old openocd setup failed/etc. Switched generator to Ninja + etc. First "full test." Fixed incorrect registry for RTC + tested success of RTC power-off retention. Note that RTC capacitor is overloaded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
2023-05-22 Lot of changes
    and I mean a lot!
    [Bill of Materials.ods]
